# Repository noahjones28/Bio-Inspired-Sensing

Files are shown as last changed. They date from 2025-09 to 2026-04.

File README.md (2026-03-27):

# Bioinspired Backbone Geometry for Continuum Robot Force Estimation

**Noah Jones**

---

## What is this?

Surgical continuum robots often brush against tissue at multiple points simultaneously. Knowing *where* and *how hard* those contacts are is critical for patient safety — but getting that information is hard. Body-mounted force sensors are bulky, hard to sterilize, and impractical at small scales. Base-mounted sensors are practical, but typically don't provide enough information to recover all the contact variables.

This project takes a different approach: **encode the missing information directly into the shape of the robot backbone.** Inspired by the evolved geometry of animal whiskers (rats, seals, elephants), we treat the backbone's cross-sectional profile as a design variable and optimize it so that a single proximal force/torque sensor can uniquely recover multiple 3D contact forces along the body.

<p align="center">
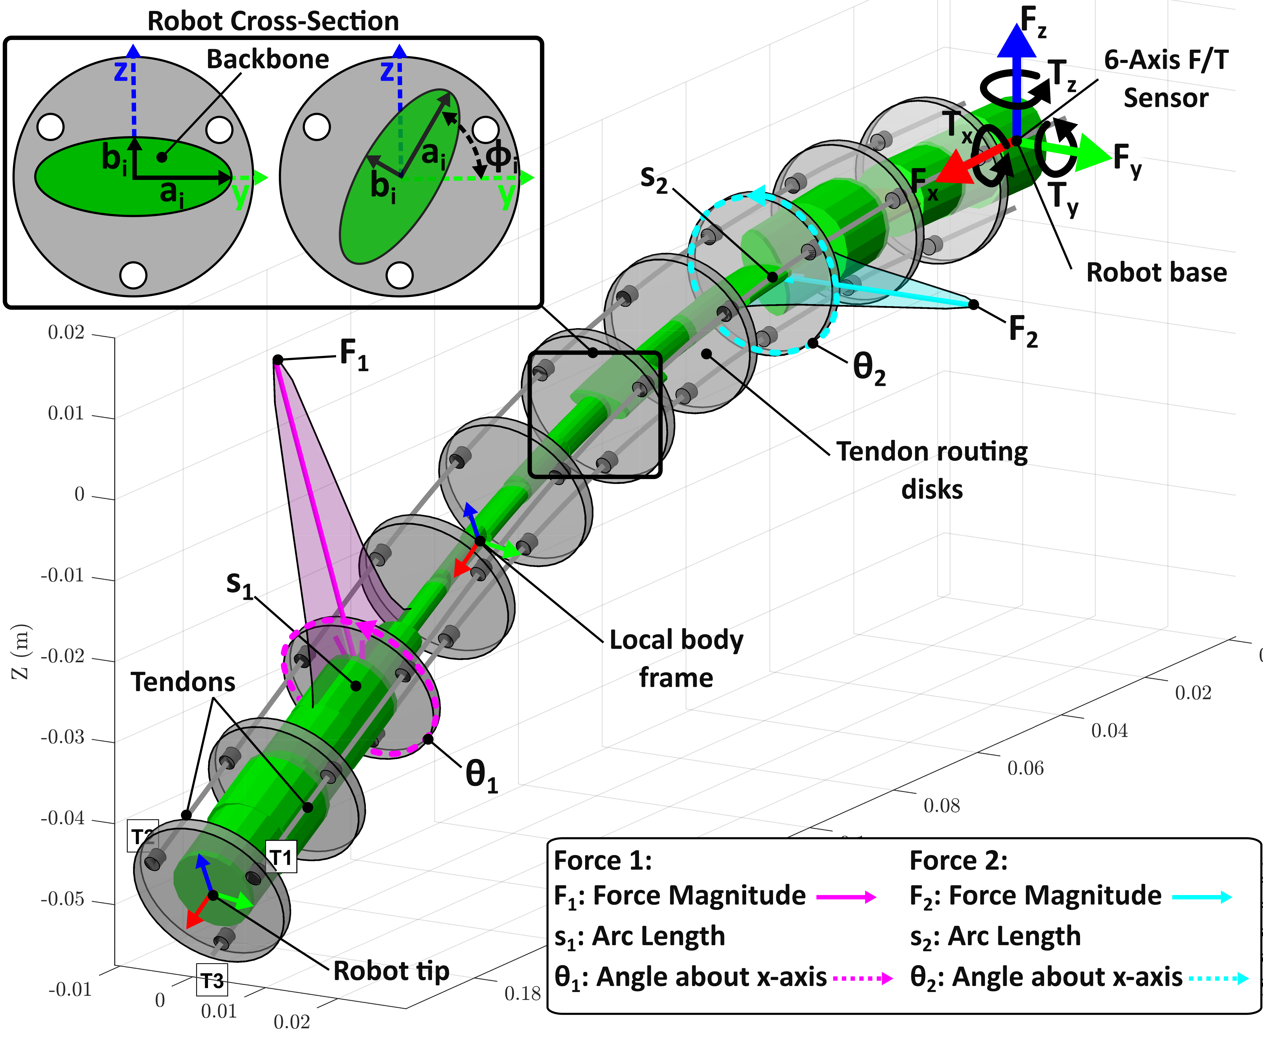
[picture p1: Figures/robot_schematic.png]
  
</p>

*The robot backbone (200 mm, 20 links) is deflected by two simultaneous point forces, each parameterized by magnitude F, arc-length position s, and angle θ. A single 6-axis F/T sensor at the base measures the resulting wrench.*

---

## Key Results

Optimized geometries dramatically outperform conventional cylindrical backbones for multi-force estimation:

<p align="center">
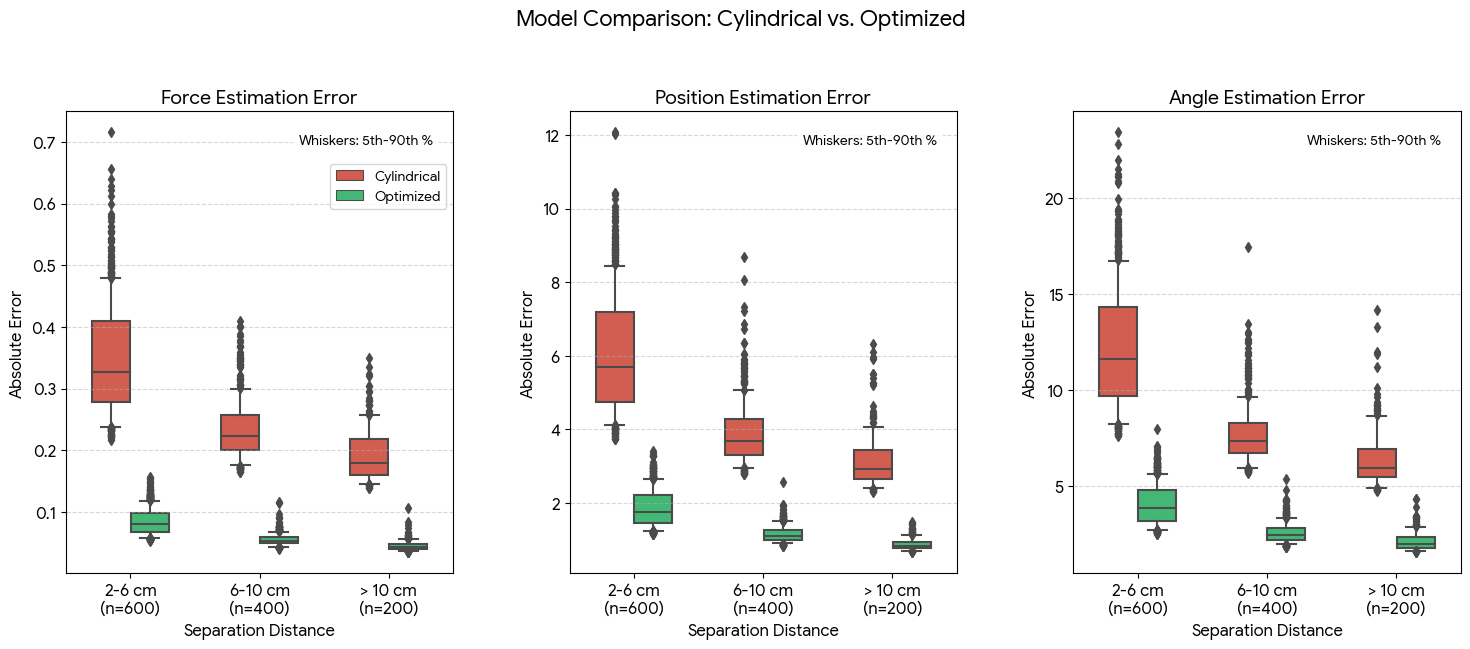
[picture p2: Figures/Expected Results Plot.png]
  
</p>

| Metric | Cylindrical | Optimized | Improvement |
|---|---|---|---|
| Mean force error | 0.22 N | 0.04 N | **~5.5×** |
| Mean position error | 4.97 cm | 0.93 cm | **~5.3×** |

---

## How It Works

### Forward Model

Each link is parameterized with an elliptical cross-section (semi-axes `a`, `b`, rotation `φ`). The backbone is simulated using **SoRoSim** (MATLAB, Cosserat rod theory). Applied forces are modeled as narrow Gaussian distributions rather than true point loads — this dramatically improves numerical conditioning in the inverse solver.

<p align="center">
  
</p>

`forward_model(F, τ)` takes applied forces and tendon tensions → returns the 6-DOF proximal wrench `[Tx, Ty, Tz, Fx, Fy, Fz]`.

### Inverse Model

`inverse_model(Wm, τm)` runs a two-stage solver to recover the forces from a measured wrench:

1. **Global search** — Latin Hypercube Sampling generates 400 candidates across the bounded design space; the 5 lowest-residual candidates become seeds.
2. **Local refinement** — MATLAB trust-region-reflective nonlinear least squares refines each seed to tolerance `10⁻¹⁰`. Best result is returned.

### Design Optimization

`design_optimization.m` searches over 60 design variables (3 per link × 20 links) to find the backbone geometry that minimizes the Jacobian condition number κ(J) — averaged over 60 randomly sampled load cases. A Von Mises safety constraint prevents plastic deformation (Bambu PC, σ_yield ≈ 62 MPa). Uses LHS global search followed by SQP (`fmincon`).

---

## Hardware

<p align="center">
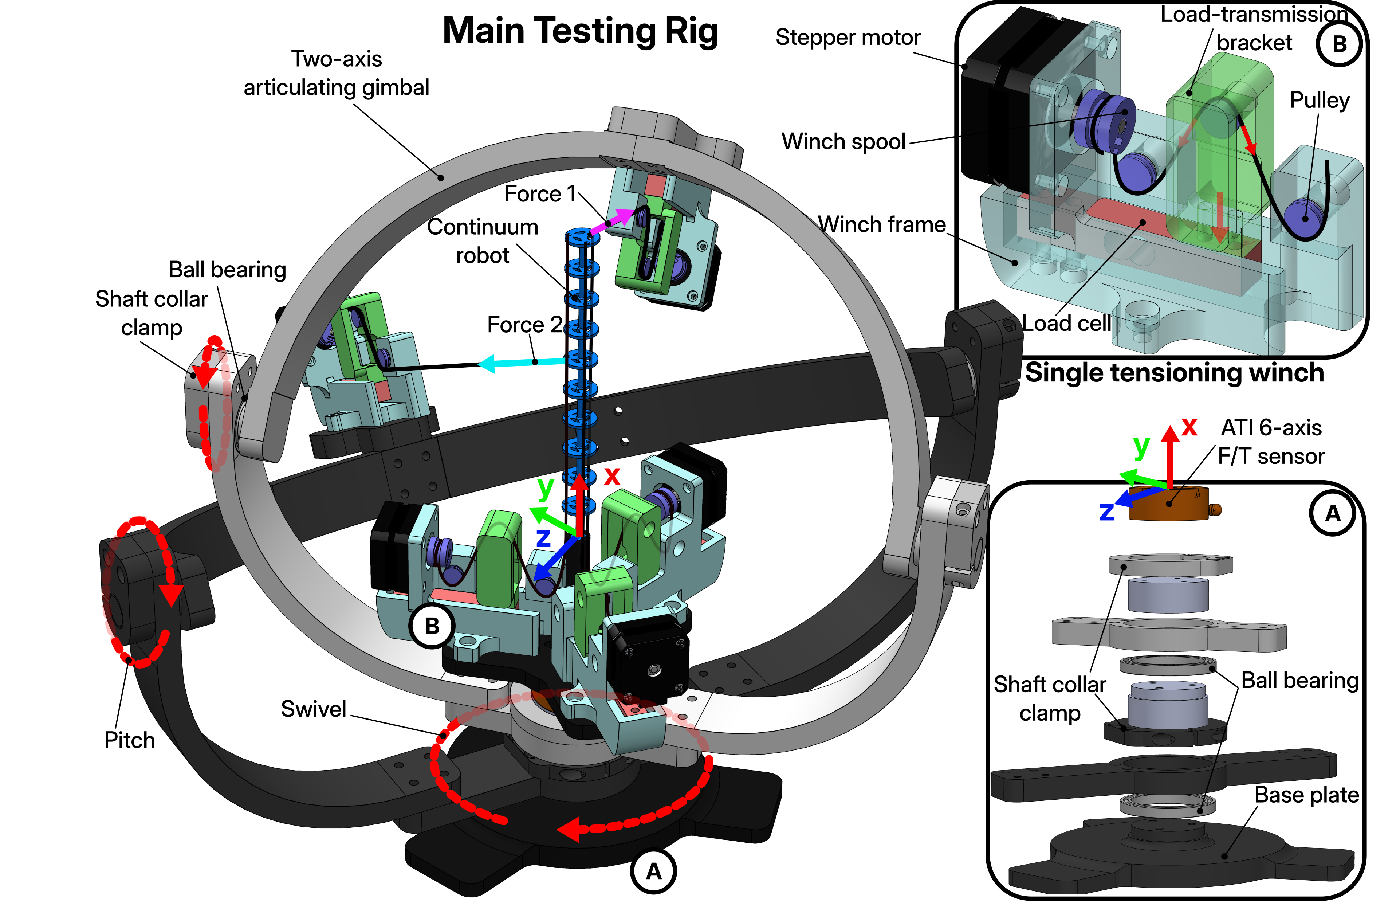
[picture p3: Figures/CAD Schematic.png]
  
</p>

The custom test rig applies two independent 3D point forces simultaneously using:

- **Two-axis articulating gimbal** for arbitrary force direction
- **5× tensioning winches** (NEMA 17 + TMC2209 drivers, 256 microstep)
- **5× 1 kg load cells** with HX711 ADCs for tension feedback
- **ATI Mini40 IP65** 6-axis F/T sensor at the proximal end
- **Arduino Mega** running the author-created control script

The backbone is FDM 3D-printed in Bambu Lab Polycarbonate (PC) on a Bambu X1 Carbon. The SolidWorks parametric model is driven by an Excel Design Table, so printing a new geometry is as simple as exporting the optimized design vector.

---

## Repository Structure

```
forward_model.m              # Applies forces + tendon tensions → proximal wrench (SoRoSim wrapper)
inverse_model.m              # Recovers forces from measured wrench (2-stage nonlinear least squares)
forward_model_parallel.m     # Parallelized forward model for batch evaluation
inverse_model_parallel.m     # Parallelized inverse model
design_optimization.m        # Backbone geometry optimizer (LHS global + SQP local)
compute_jacobian.m           # Finite-difference Jacobian ∂W/∂F
apply_gaussian_force.m       # Converts point loads to discrete Gaussian distributions
calc_ellipse_vonmises.m      # Von Mises stress for elliptical cross-sections (safety check)
global_to_local.m            # Coordinate frame transforms
update_design.m              # Applies a design vector to the SoRoSim robot model
plot_robot.m                 # Visualizes deflected backbone, tendons, and applied forces
jacobian_tester.m            # Validates Jacobian computation
copyHandle.m                 # Deep copy for MATLAB handle objects
my_robot.mat                 # Saved baseline robot configuration

Arduino/                     # Arduino Mega control script (winches + load cells)
ATI Sensor Calibration/      # ATI Mini40 calibration files
CAD/                         # SolidWorks parametric backbone and test rig models
Figures/                     # Publication figures
Optimization Results/        # Saved optimizer outputs
my_robots/                   # Saved SoRoSim robot configurations
```

---

## Dependencies

- MATLAB R2023+ with:
  - [SoRoSim toolbox](https://github.com/SoRoSim/SoRoSim)
  - Optimization Toolbox (`fmincon`, `lsqnonlin`)
  - Statistics and Machine Learning Toolbox (Latin Hypercube Sampling)
- Arduino IDE (for hardware control)

---

## Citation

```bibtex
@mastersthesis{jones2025whisker,
  title  = {Bioinspired Backbone Geometry for Continuum Robot Force Estimation},
  author = {Jones, Noah},
  school = {University of California San Diego},
  year   = {2025}
}
```

---

**Noah Jones** · noah@familiajones.org

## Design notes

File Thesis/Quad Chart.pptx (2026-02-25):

## Bio-Inspired Backbone Geometry for Multi-Point 3D Force Estimation in Continuum Robots

- Problem

- Approach

- Results

- Significance

Noah Jones, T.K. Morimoto

- Motivation: Knowledge of robot-tissue interaction forces during surgery can reduce patient injury and improve quality of surgeon’s force feedback.
- Goal: Estimate the magnitudes and locations of multiple point forces.
- Body-Mounted Sensing (FBGs, EM, Resistive flex):
- Pros: Very accurate Cons: Hard to sterilize, bulky, hard to integrate [1].
- Visual-Based Sensing (Endoscopic cameras, fiducial tracking) :
- Pros: Can resolve multiple point forces with high accuracy [2][3], easy to sterilize.
    - Cons: Requires direct line-of-sight of robot body, camera space constraints.
  - Proximal-Mounted Sensing (force/torque sensors, Tendon tension sensors):
    - Pros: Works in blind environments, easy to sterilize, easy to integrate [4]
    - Cons: Current approaches cannot resolve magnitudes and locations of multiple point forces (ill-posed inverse).

- Design Evaluation: We compare designs numerically and graphically using manipulability ellipsoids. Superior geometries maximize the shortest axis (minimum singular value), ensuring sensitivity in all directions.
- Experimental Validation: For inter-force separations greater than 8 cm, the optimized design achieves median absolute errors of approximately 0.05 N, 1.0 mm, and 2.2°—corresponding to performance improvements of 74%, 67%, and 66% respectively over the cylindrical baseline. Performance gains diminish at smaller separations but remain measurable.

- Idea: We propose estimating multiple point forces using proximal sensors and variations in robot backbone geometry.
- Inspiration: Sensory appendages in animals (whiskers, antennae) use non-circular cross-sections and mass asymmetry to mechanically amplify weak signals—like torsion—that would otherwise be masked by dominant bending modes [5]. These geometries help overcome the ill-posed nature of multi-force sensing in straight cylindrical designs [6][7].
- Method: We develop an optimization framework to find backbone geometries that maximize multi-contact force estimation accuracy. The backbone is modeled as a series of elliptical cross-sections, with the major and minor radii of each segment as design variables. The objective is to find geometries with well-conditioned Jacobians—ensuring sensor noise is not amplified into large force estimation errors.

- Sensing Through Shape: Just as natural selection has shaped animals' sensory appendages to optimize perception for their specific environments, we extend this principle to design tendon-driven surgical robots with geometries tailored to the complex loading conditions they encounter.
- Optimization: We show how optimization can be used to find an optimal backbone design, capable of resolving multiple point-loads that conventional cylindrical backbones cannot due to inherent sensing degeneracies.
- Hardware Testing: We develop a custom testing rig featuring multiple PID controlled tensioning winches and a two-arm gimbal, capable of applying 3 tendon tensions, and 2 point-forces in 3D.

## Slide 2

References

1. Gao, Anzhu, et al. "Body contact estimation of continuum robots with tension-profile sensing of actuation fibers." IEEE Transactions on Robotics 40 (2024): 1492-1508.
2. Aloi, Vincent, et al. "Estimating forces along continuum robots." IEEE Robotics and Automation Letters 7.4 (2022): 8877-8884.
3. Ferguson, James M., D. Caleb Rucker, and Robert J. Webster. "Unified shape and external load state estimation for continuum robots." IEEE Transactions on Robotics 40 (2024): 1813-1827.
4. Sadati, SM Hadi, et al. "Stiffness imaging with a continuum appendage: Real-time shape and tip force estimation from base load readings." IEEE Robotics and Automation Letters 5.2 (2020): 2824-2831.
5. Mohren, T. L., et al. "Coriolis and centrifugal forces drive haltere deformations and influence spike timing." Journal of the Royal Society Interface 16.153 (2019): 20190035.
6. Starostin, E. L., V. G. A. Goss, and G. H. M. van der Heijden. "Whisker sensing by force and moment measurements at the whisker base." Soft Robotics 10.2 (2023): 326-335.
7. Huet, Lucie A., John W. Rudnicki, and Mitra JZ Hartmann. "Tactile sensing with whiskers of various shapes: Determining the three-dimensional location of object contact based on mechanical signals at the whisker base." Soft robotics 4.2 (2017): 88-102.

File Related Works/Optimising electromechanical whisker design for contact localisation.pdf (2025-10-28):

Sensors & Actuators: A. Physical 376 (2024) 115591 (https://doi.org/10.1016/j.sna.2024.115591)

## Available online 12 June 2024

0924-4247/© 2024 The Authors. Published by Elsevier B.V. This is an open access article under the CC BY license (http://creativecommons.org/licenses/by/4.0/).

Contents lists available at ScienceDirect (https://www.journals.elsevier.com/sensors-and-actuators-a-physical)

# Sensors and Actuators: A. Physical

journal homepage: www.journals.elsevier.com/sensors-and-actuators-a-physical

## Optimising electromechanical whisker design for contact localisation

## Simon P. Pegoli a,∗ , Phillip S.M. Skelton a,b , Russell S.A. Brinkworth a

a Centre for Defence Engineering Research and Training, Flinders University, Tonsley, SA, 5042, Australia
b Faculty of Science, Technology, Engineering, and Mathematics (STEM), University of South Australia, Mawson Lakes, SA, 5095, Australia

A R T I C L E I N F O

Keywords:
Electromechanical whisker
Vibrissae
Tactile sensing
Bio-inspired sensing
Object localisation
Robotic mapping

A B S T R A C T

Electromechanical whiskers are inexpensive and useful tactile sensor systems for robotic mapping tasks within environments problematic to image and range sensors. This research aims to quantify the effect of the whisker’s mechanical properties on its ability to achieve accurate contact localisation. Using mechanical beam theory, a model relating the rate of change of a whisker’s strain as a result of the location of a radial contact was derived. A more practical linear approximation of this model was then created with an operating range for which a whisker was theoretically capable of performing contact localisation within 0.1% error. These models facilitated the design of theoretically optimal whiskers. It was discovered that the longer the whisker, and the closer the strain-measuring sensor was placed towards the whisker base, the greater the required taper. For larger whisker widths and faster contact speeds, a smaller taper was required. Additionally, whiskers tapered in 2 dimensions required larger tapers than one-dimensional tapers to achieve optimal performance. The presence of a central hollow region (medulla) did not have a practical effect on the required taper or the performance of the whisker. Experimental results showed that a 200 mm whisker with an optimal taper derived from our model was able to measure the location of contacts with an error less than the target 0.1% anywhere in the distal 58 mm, with a response time of 0.1 s. Tapering electromechanical whiskers to their derived optimal value enhances the accuracy and efficiency of whisker-based robotic mapping.

### 1. Introduction

The ability for mobile robots to autonomously plan and execute navigation using knowledge of their surroundings gathered from on-board sensors has enabled them to be effective in many modern day affairs including inspection [1], search and rescue [2], entertainment [3] and sanitation [4], among many others. The simultaneous localisation and mapping (SLAM) method is used to informedly perform live navigation based on an environment map generated simultaneously using on-board sensors and robotic mapping [5].
The majority of modern robotic mapping approaches utilise optical rangefinders (e.g., light detection and ranging sensors) or vision sensors (e.g., cameras) [6]. Robotic mapping can be enhanced through the implementation of tactile sensing in environments notoriously precarious for optical sensing, including those containing occluded and concealed objects [7,8], compliant and/or malleable bodies [9], particulate air [10] and reflective and/or transparent surfaces [11]. A major disadvantage of tactile sensors is their comparatively shorter search range than optical or visual sensors due to their reliance on physical interaction with external bodies [12]. However, in contrast to range and imaging sensors, whiskers are not only inexpensive and

∗ Corresponding author.

E-mail address: simon.pegoli@flinders.edu.au (S.P. Pegoli).

simple to construct, but require significantly less computational power to operate.
Mammalian facial whiskers (vibrissae) are tactually-sensitive hairs that provide tactile exteroception in almost all mammals [13]. Many small quadrupedal mammals use the information from vibrissae to guide locomotion [14]. Rats commonly feature arrays of between 30 to 35 macrovibrissae of length ranging between 4 mm and 50 mm on either side of the snout [15,16] (2%–23% of the mean length of the brown rat, 217 mm [17]). Rat whiskers can be approximated as truncated cones, and contain a low density region known as the medulla within the proximal portion [18]. The tapered profile enables whiskers to slip past objects once a critical bending angle has been realised [19], enhancing mobility through cluttered environments, whilst the medulla reduces sagging due to gravity [20]. The length and diameter of both the cuticle and the medulla vary based on the location of the whisker on the mystacial pad, and has been quantified in [21]. The formation of whiskers on the mystacial pad forms 2 search volumes on either side of the snout with a shape resembling sections of spheres centred about the rat’s eyes [22]. Rats will actively sweep (whisk) their whiskers in front of them in the azimuth direction to induce light contacts with external objects [23,24], further expanding the whisker search

https://doi.org/10.1016/j.sna.2024.115591
Received 20 February 2024; Received in revised form 18 May 2024; Accepted 9 June 2024

## Sensors and Actuators: A. Physical 376 (2024) 115591

S.P. Pegoli et al.

volume. Behavioural studies indicate that rats will whisk in a manner to purposefully make contact at radial locations near to, and at, the whisker tip [24].
Two different types of mechanoreceptive cells are located in the whisker follicle, allowing for the detection of both the magnitude and rate of change of the whisker deflection [25,26]. Neurological processing of the mechanoreceptor signals, proprioceptive knowledge of whisker locations on the snout, and the timing of the contact during the whisk cycle allows rats to determine the spatial location of a contact [27,28]. Through this, rats can recognise both the shape [15] and orientation [29] of objects.
Contacts made on an electromechanical whisker can be localised by deciphering the mechanical response of the whisker measured by a variety of sensors. Selection of the sensor device(s) used, the whisker shaft material, and the manufacturing process are key design choices for electromechanical whiskers, and are often intertwined. Following the foundational concept that animal nervous systems are more adept at measuring the rate of change of signals rather than their absolute magnitude, the rate of change of the whisker strain [30] or the bending moment [31] collected by strain gauges can be converted to a contact location for whiskers arranged as cantilever beams. In the case of the whisker strain, this holds true as long as the whisker undergoes small deflections, e.g., less than 10 degrees [30]. Similar outcomes can be achieved through measurement of the pressure on a load plate perpendicular to the whisker shaft using barometers [32,33] and piezoresistors [34]. Measurement of the degree of deformation throughout the whisker shaft can be used, achievable by measuring the wavelength shift due to bending of optical fibre [35]. For a hinged whisker, the displacement of the whisker base in multiple dimensions can be used to convert whisker shaft deformation into a contact location using Hall effect sensors [36,37]. A hinged whisker is seemingly more complex to develop than a cantilever beam due to the requirement for an automatic return system, which can be especially challenging to achieve at small scales. Many other designs utilising different sensing modalities also exist (see [38] for a recent review covering electromechanical whisker designs). In all of these cases, the signal magnitude varies non-linearly with the contact location.
The whisker shaft can be manufactured simply as beams from plastic rods [32,34] or metal wires [31,37]. Curvature can be achieved through heat-forming [37]. 3D printing [33,39] and moulding [30] allows for precise manufacturing of whiskers with various shapes. Thermoplastics often used in 3D printing, such as acrylonitrile butadiene styrene (ABS), possess favourable mechanical properties which allow whiskers to deflect elastically at large angles (up to at least 50 degrees) without permanent (plastic) deformation [40], which can be useful for operation within confined spaces. Fibre drawing of thermoplastics can achieve desired tapering of whiskers at smaller scales than conventional fused deposition modelling [40]. The whisker can be formed entirely from the sensor system itself, as in the case for optical fibre whiskers [35], and embedding such sensors within a material can control its deformation properties whilst protecting the sensor from the external environment [41,42].
Maps can be generated using electromechanical whisker sensing through the collection of localised contact locations in space over the duration of a navigation mission. Contour fitting allows for the reconstruction of object shapes using localised whisker contact points [8,31,35]. Modelling of a robot’s searched environment can be achieved through population of an occupancy map using recorded whisker contact points, achievable using SLAM techniques [43–45]. Texture sensing is another heavily explored application with electromechanical whiskers, allowing for discrimination of objects based on their surface smoothness [46–48].
Both the bending moment and the strain along the whisker increases in direct proportion to the whisker’s base diameter and the contact speed [30,31]. As the width of the whisker increases, however, so will its rigidity [49]. For rats, the conical whisker taper is an important functional feature as this allows objects to conveniently slip past the whisker without inducing large, potentially damaging bending angles, enabling agile mobility within their typically confined and cluttered habitats [19,50]. Untapered whiskers will also frequently become stuck inside the grooves of textured surfaces, whereas tapered whiskers, especially conical, will undergo characteristic stick–slip behaviour, indicating a greater applicability of tapered whiskers to feature sensing [50]. For electromechanical whiskers, the three-dimensional (3D) contact location can be uniquely calculated using the combination of the axial force, the bending moment magnitude, and the direction of the bending moment measured at the whisker base, as long as the whisker is tapered [51]. 3D contact localisation has been found to be more accurate for tapered whiskers than untapered whiskers when using these same mechanical measurements [40]. A ‘‘sweet spot’’ between the location of object contact and the contact speed for which discrimination of contacts are more easily achieved is suggested to exist [52]. However, this balance has not been identified across the various parameters that make up a whisker system.
Aside from these observations, the impact of an electromechanical whisker’s geometry and other design/functional parameters on its capability to localise contacts has, to the best of our knowledge, yet to be quantified. The goal of this research was to universally quantify the optimal balance between whisker length, thickness, taper, and whisk speed for achieving accurate contact localisation. The impact of the presence of a medulla was also explored. This was with specific interest towards whisker systems that can achieve accurate localisation as efficiently as possible, requiring minimal computing resources for signal processing. This knowledge will enable roboticists to efficiently design electromechanical whisker systems that can attain optimal contact localisation results, improving robotic mapping outcomes.

### 2. Materials and methods

### 2.1. Whisker parameters and nomenclature

Figs. 1(a) and 1(b) show, respectively, the front and top view of a schematic electromechanical whisker of length lw, base width wb

, and
tip width wt undergoing contact by an object at distance l
c

from the
whisker base with contact speed vc

. Our approach treated whiskers as straight, homogeneous, flexible cantilever beams due to the simplicity in manufacture of a cantilever whisker compared to a hinged whisker. In a similar fashion, the whisker strain, measurable through a single sensor element such as a strain gauge placed at a distance l
s

from the
whisker base, was used as the sensory input for contact localisation as this requires straightforward assembly with simple circuitry and signal processing as opposed to other methods.
The whisker’s taper magnitude (T ) was defined as the ratio of the cross-sectional area of the outer shape of the whisker base (Ab
) to
the cross-sectional area of the outer shape of the whisker tip (At ),
disregarding any holes present in either of the cross-sections, as per Eq. (1).

T =

Ab
At

(1)

We explored 2 categories of whisker taper: (1) tapered in a single dimension (T1D); and (2) tapered in 2 dimensions (T2D). A T1D whisker was one whose height remains constant but whose width decreases along the whisker length (represented as a dashed line in Fig. 1). A T2D whisker was one in which both the width and the height decreased uniformly along the whisker length (represented as a solid line in Fig. 1), e.g., a cone. Whiskers with no taper (i.e., T = 1), e.g., a cylinder, were classified as untapered (T0D). This research only considered whiskers with a linear taper with the base’s external cross-section having regular shape (i.e., a regular polygon or a circle). Both T1D and T2D taper types were explored as we hypothesised that they would each provide distinct advantages in different situations. T1D whiskers, being more

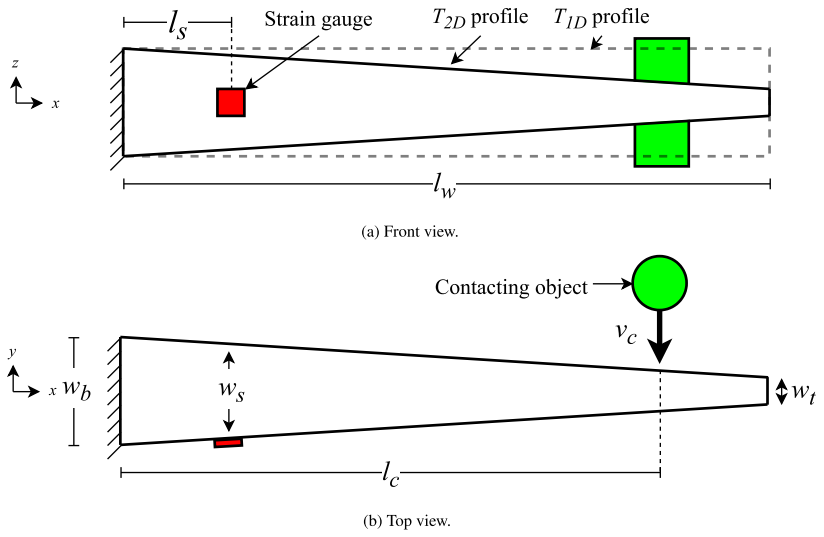
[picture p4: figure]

Fig. 1. Schematic of a T1D (dashed profile) and T2D (solid profile) whisker of length lw, base width wb and tip width wt , undergoing contact at length l
c

from the whisker base
at contact speed vc
. l
s

represents the distance between the whisker base and the centre of the sensing element, with ws being the width of the whisker at this location. (a) Front view. Only T2D whisker tapers in height. (b) Top view. Both T1D and T2D whiskers taper in width.

flexible in the direction of the contact (y axis) than in the perpendicular
direction (z axis), would be expected to be more suitable to applications
where only unidirectional contacts were of interest, as deflection in the perpendicular direction would be more restricted. T2D whiskers, being flexible in both the y and z directions, were expected to be more suitable for measuring contacts occurring in both planes.

### 2.2. Derivation of whisker strain relationship to contact location

Under the assumption that the contacting object is rigid and applies a point load to the whisker during contact, the Euler–Bernoulli beam equation [49] can be used to derive a numerical relationship between the whisker strain and the contact location. For a small deflection in the y direction (s) at the contact location (l
c

) arising from a point load (F) (e.g., a rigid body contact), the curvature (κs

) of a cantilever beam
(whisker) measured at a point on the whisker face along the x axis (l
s

)
is given as:

κs ≈

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
c − l
s

)
EIs
, | (2)

where Ms

is the moment at point l
s
| , E is the Young’s modulus of
the whisker, and Is

is the second moment of area at point l
s
| in the
direction perpendicular to the contact. Study of the geometry of tapered beams shows that the width of the whisker at the sensor location (ws
| )
is related to the whisker base width (wb | ), total length (lw), and the
distance of the sensor from the base (l
s

) by:

ws1D

= wb

(
1 +

l
s
lw

(1∕T − 1)

)
| (3a)

ws2D

= wb

(
1 +

l
s
lw

(√

1∕T − 1)) | (3b)

where ws1D

is the whisker width at the sensor location for a T1D whisker, and ws2D

is that for a T2D whisker. Is | can therefore be written
as the product of the second moment of area at the whisker base (Ib
| )
and the scale of diversion of the second moment of area at the sensor location from that at the whisker base (∇I), as in Eq. (4):
Is = Ib∇I | (4)

∇IT1D

=

(
1 +

l
s
lw

(1∕T − 1))3
(4a)

∇IT2D

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
1∕T − 1))4
(4b)

where ∇IT1D

is the scale of diversion of the second moment of area at the sensor location from the whisker base for a T1D whisker, and ∇IT2D is that for a T2D whisker. This relationship holds true for both solid and hollow whiskers, as long as the taper magnitude of the hollow geometry matches the taper magnitude of the whisker’s shaft.
Substituting Eq. (4) into Eq. (2), taking the definite integral from points 0 to l
s

twice to solve for the whisker displacement, and solving for the contact location, an equation for the deflection at the contact location (sT

) can be obtained for both taper classes:

sT1D

(l
c

) =

F lw(a1

2
l
c

2 + 2lw

2
(ln(a1
l

c + lw) − ln(lw)) − 2a1
l
c

lw)
2a1

3EIb

(5a)

sT2D

(l
c

) =

F lc

2
lw(2l
c

2
a2 + 2l
c

lw)
6EIb

(l

ca2 + lw)

2

(5b)

where a1 = 1∕T − 1 and a2 =

√
1∕T − 1. The whisker strain at the sensor location (εs

) is related to the moment at l
s

(Ms

), section modulus
at the sensor location (Zs

), and Young’s modulus of the whisker (E) by Eq. (6):

εs =

Ms
ZsE

=

F(l

c − l
s

)
ZsE

(6)

Rearranging Eq. (6) for F and substituting into Eq. (5), the displacement at the contact location can be expressed in terms of the whisker strain measured at the sensor location:

sT1D

(l
c

) = εs ×

lwZs

(2lw

2
ln(a1
l

c + lw) + a1
l
c

(a1
l

c − 2lw) − 2lw

2
ln(lw))
2a1

3Ib
(l

c − l
s

)
(7a)

sT2D

(l
c

) = εs ×

l
c

3
lwZs
3Ib

(l

c − l
s

)(l

ca2 + lw)

(7b)

Solving Eqs. (7a) and (7b) for εs and taking the time derivative on both sides, the relationship between the rate of change of strain ( ̇εs )
and the whisker contact location is:

̇εsT1D

(l
c

) = vc ×

2a1

3Ib
(l

c − l
s

)

lwZs

(2lw

2
ln(a1
l

c + lw) + a1
l
c

(a1
l

c − 2lw) − 2lw

2
ln(lw))
(8a)

̇εsT2D

(l
c

) = vc ×

3Ib

(l

c − l
s

)(l

ca2 + lw)

l
c

lwZs

(8b)

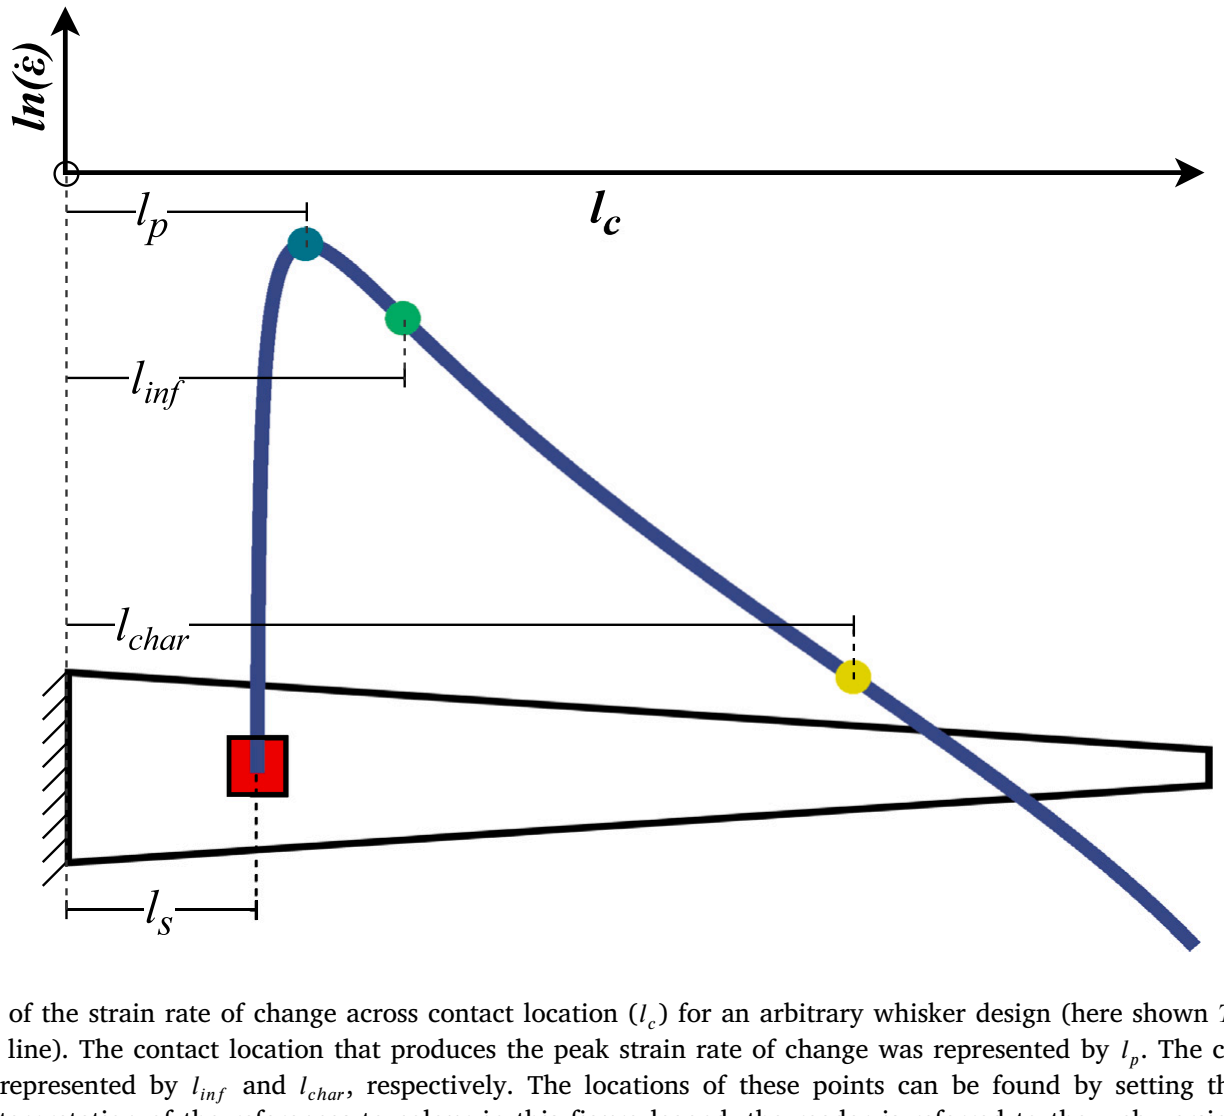
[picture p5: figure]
inf and l

Fig. 2. General shape of the logarithm of the strain rate of change across contact location (l
) for an arbitrary whisker design (here shown T2D taper, refer to Section 2.1) overlaid over the whisker (blue solid non-linear line). The contact location that produces the peak strain rate of change was represented by lp

. The contact locations of the first and second (characteristic) inflection points were represented by l

cℎar , respectively. The locations of these points can be found by setting the first (lp

) and second (l

inf and l
cℎar )
derivatives of Eq. (8b) to zero. (For interpretation of the references to colour in this figure legend, the reader is referred to the web version of this article.)

If the contact velocity (vc

) is known, which is achievable by performing controlled motorised whisks, solving Eqs. (8a) and (8b) for l
c
can therefore be used to deduce the contact location from the rate of change of the whisker strain at location l
s

for small whisker deflections. It is important to note that Eq. (8a) is invalid for a T0D whisker as it means a1 = 0, which results in ̇εsT1D

= 0, which is untrue. Therefore Eq. (8b) must be used for untapered whiskers. It is also important to note that the shape of the whisker’s cross-section does not feature in the equations. Therefore, the rate of change of the strain is independent of the cross-sectional shape for whiskers within the same taper class which have a uniform taper. Additionally, Eqs. (8a) and (8b) show that ̇εs does not depend on the whisker’s material (i.e., the Young’s modulus). This is as the equations assume that the whisker’s (or inversely the object’s) translational velocity remains constant during the contact, and that the bending of the whisker during the contact does not contribute to a reduction in this velocity. This is practically suitable assuming that the contacting object is rigid and the whisker is flexible enough to not undergo plastic deformation from the applied displacement.

### 2.3. Linearising the model

Fig. 2 shows the general shape of the logarithm of the strain rate of change across contact location curve for a whisker of arbitrary length, taper, width, and sensor location.
The shape of the logarithm of the strain rate of change across contact location reveals three fundamental points along the curve: Location of the peak strain rate of change lp

; location of the first inflection point l

inf ; and location of the second inflection point l

cℎar. Firstly, the strain
rate of change rapidly increases for contact locations further along the whisker length than the sensor location before reaching a peak at location lp

, for which the strain rate of change decreases beyond. The contact location producing this peak indicates the lower limit of the total operating range of the whisker, as contacts towards the whisker base from this point will produce non-unique strain rate of change with contacts towards the whisker tip, making the contact location ambiguous.
The first inflection point, l

inf , exists a short distance following the peak. However, its value was not important to our method. The second

inflection point, l

cℎar, exists towards the whisker tip. This second inflection point was of importance for obtaining a linear approximation of the whisker’s strain rate of change across contact location, and will henceforth be referred to as the characteristic inflection point. Deriving a linear approximation centred at this point will create a linear operating range towards the whisker tip, which was desirable for mapping purposes.

The linearised model of the logarithm of the strain rate of change across contact location was calculated for T0D, T1D and T2D whiskers as the first order Taylor series centred about the whisker’s characteristic inflection point. The operating range for a whisker’s linear model was defined as the region of the whisker for which the percent error between the strain rate of change curve and the first order Taylor series approximation was within 0.1%. This maximum error was selected to promote high accuracy within the entirety of the linear operating range.

A whisker’s optimal taper (T

∗
) was defined as that which possessed the widest linear operating range that included the whisker tip, thus maximising the operating range. This range also enables mimicry of rat whisker placement behaviour which is biased towards contacts near and including the tip [24]. T

∗ was calculated by finding the smallest whisker taper that possessed a linear operating range whose upper limit was located exactly at the whisker tip. Generalised mathematical models describing T

∗
, the corresponding size of the linear operating range (W ∗
) and location of the characteristic inflection point (l

∗
cℎar),
were developed by calculating these values for whiskers of varying length, sensor location, base width and contact speed for both T1D and T2D whiskers. The sensor location was limited to within 1/8th of the whisker length from the base as sensors placed within this region would have reduced potential for collision with objects during robotic mapping tasks.

The effect of deviating from the optimal taper on whisker-based robotic mapping was observed by plotting the linear operating size range against the proportion of whisker taper against the optimal whisker taper. This was performed for both T1D and T2D whiskers across varying sensor location, whisker length, base width and contact speed.

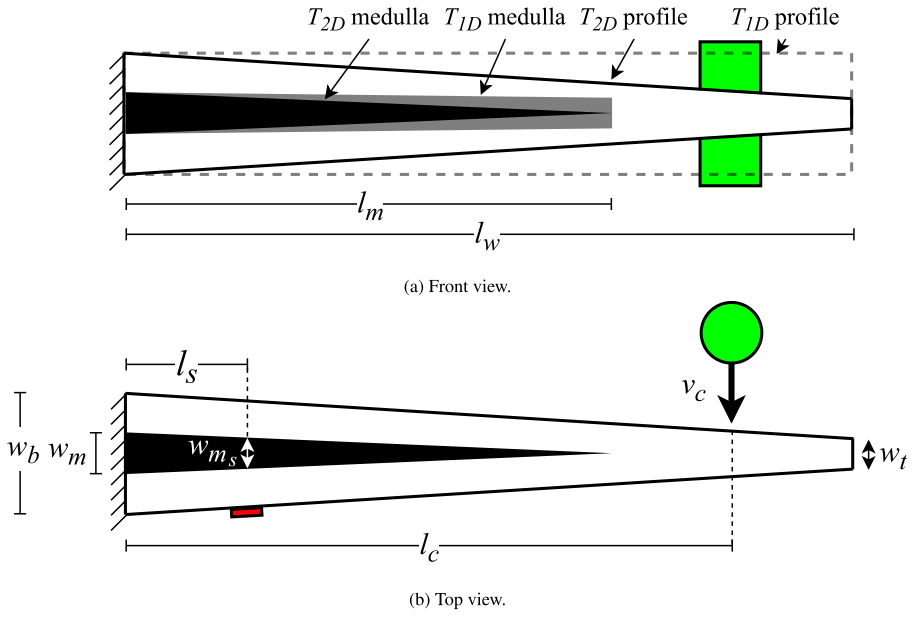
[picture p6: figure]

Fig. 3. Schematic of the central cross-section of whiskers with a biologically mimetic medulla (shaded area) with base width wm and length lm
. The darker shaded region shows the shape of the medulla for T2D whiskers, and the lighter shaded region shows the shape of the medulla for T1D whiskers. The width of the medulla at the sensor location is denoted wms

. (a) Front view. The medulla for T2D whiskers tapers to a point, but the medulla for T1D whiskers tapers to an edge. (b) Top view. The medulla for both T1D and T2D whiskers taper in width.

### 2.4. Exploring the medulla

The effect of a biologically mimetic medulla on whisker performance was explored mathematically. Here, whiskers were now modelled to contain a medulla as a tapered, hollowed-out region centred about the central axis of the whisker. The medulla’s cross-section had the same shape of the cross-section of the whisker shaft, with the widest point at the base, and tapered linearly with the same taper dimensionality as the whisker shaft (i.e., a 1D taper for T1D whiskers and a 2D taper for T2D whiskers) up to an edge (for T1D whiskers) or a point (for T2D whiskers), at a distance lm from the whisker base. Fig. 3 shows the central cross-section of a whisker containing a medulla, showing these parameters. The base width of the medulla (wm), and the length of the medulla (lm), were fixed for any given whisker based on Eqs. (9a) and (9b) respectively, selected based on the average medulla proportions for the column of caudal-most whiskers on the rat snout (i.e., the longest whiskers) [21]. This resulted in the width of the medulla at the sensor location (wms

) being related to the whisker base width, length and sensor location by Eq. (9c).

wm = 0.324wb

(9a)

lm = 0.786lw | (9b)

wms

= wb

(
0.324 − 0.415

l
s
lw

)
| (9c)

The scale of diversion of the second moment of area at the sensor location from that at the whisker base for whiskers not containing a medulla (∇I) was no longer equal to the relationships of Eqs. (4a) and (4b) for whiskers containing a medulla where the taper magnitude of the whisker was such that the slope of the whisker shaft did not match the slope of the medulla. The scale of diversion of the second moment of area at the sensor location from that at the whisker base was derived for T1D and T2D whiskers containing medullae (∇Im), and the ratio of (∇Im) to ∇I for whiskers of the same taper class was taken to quantify the impact of the addition of the medulla on this parameter (see Appendix A for the algebraic derivations of these). This revealed that ∇Im was practically equivalent to ∇I, and therefore Eqs. (8a) and

(8b) were deemed appropriate for calculating the strain rate of change of the whisker due to a contact for whiskers possessing a medulla. The optimal taper, operating range, and characteristic inflection point was modelled for whiskers possessing a medulla using the same method as in Section 2.3. The effect of the medulla on these parameters was quantified by calculating the root mean square error (RMSE) between the models for whiskers with a medulla to those without medullae.

### 2.5. Simulations

Transient structural analyses were performed in Ansys Mechanical 2021 R2 to verify the correctness of the derived strain-contact location relationship. Whiskers were fixed at the base using a fixed body-ground joint, and an 8 mm diameter steel cylinder was driven radially into the whiskers with constant speed at various contact locations (refer to Section 2.1 and Fig. 1 for more details). A cylinder was used to produce a constant translational deflection at a point on the whisker whilst allowing the whisker to slip smoothly past it as it deforms. Note that this causes the contact location to slide towards the whisker tip as the whisker deforms. As we were only interested in the strain relationship over small deflections, the effect of this slippage was negligible. The strain along the whisker length on the side opposite to the contact was measured across time, which was then used to calculate the strain rate of change at potential sensor locations.
Two variations in the whisker cross-sectional shape were studied for the three taper classes (T0D, T1D and T2D) to check for consistency in results for varying whisker profiles. For T0D whiskers, both cylindrical and square prisms were studied. For T1D whiskers, whiskers were designed as a square base tapering to a rectangular tip and a circular base tapering to an ellipsoidal tip (both with constant heights). For T2D whiskers, truncated square pyramids and truncated cones were studied. Three different whisker base widths were simulated to observe the effect of the whisker width: 4.5 mm, 6 mm and 8 mm. These widths were selected as whiskers could be reliably manufactured at these widths for comparison between simulation and hardware.
The resulting strain rate of change data from the simulation results were plotted against the theoretical model to observe the closeness

Table 1
Materials and their respective Young’s modulus (as quantified in Ansys) used in the simulations to determine the effect of whisker material on the strain rate of change.
Material | ABS | PLA | Epoxy resin | Beech wood | Aluminium alloy | Structural steel
Young’s Modulus [GPa] | 2.41 | 2.94 | 3.78 | 12.93 | 71 | 200

of the simulation results to theory. The coefficient of determination (R²
) and RMSE were calculated for each whisker taper to quantify the alignment of the simulation results to the theory.
Simulations were additionally performed to determine whether there was an impact on the strain rate of change relationship with the contact location due to the whisker’s material. The strain at the sensor location was recorded for whiskers of equivalent dimensions but made from different materials. The materials tested, and their Young’s modulus (recorded from Ansys), can be found in Table 1. The resulting strain rate of change during the initial contact period (i.e., small deflection period) was compared for equivalently shaped whiskers of different materials for contacts made at the same location.

### 2.6. Hardware experiments

Experiments were performed with a manufactured ABS whisker with optimal T2D taper to observe the performance of a theoretically optimal whisker in performing contact localisation using the developed linear approximation method. The whisker was manufactured as a truncated square pyramid with wb=4.5 mm and lw=200 mm through fused deposition modelling 3D printing. This method allowed for inexpensive and repeatable whisker production. An alternative approach of printing whiskers from inexpensive resin was found to limit their use in confined spaces due to their tendency to snap at smaller angles than ABS whiskers, and was therefore not used. While specialist resins may have been available, their cost would have been prohibitive. Derivation of the taper magnitude used for this whisker can be found in Section 3.3. A truncated square pyramid was used to promote deflection in the x-y plane and hinder deflection in the x-z plane from a contact in the y direction (see Fig. 1(b)) whilst resembling the T2D geometry seen in rat whiskers. The whisker length was selected such that the whisker could be useful for robotic mapping when aboard a small mobile robot, where a maximum detection range of 200 mm would be sufficient for object avoidance and to cover potential dead zones of LiDARs. The base width selected was the minimum practical base width that allowed for adhesion of a strain gauge (Tokyo Measuring Instruments Lab model FLAB-5-11-1LJC-F) at a sensor location of l

s = 20 mm. This
was the lowest practical sensor location within the targeted bottom 1/8th of the whisker length due to the strain gauge dimensions and wire routing considerations. The strain gauge was wired to an arm of a balanced quarter Wheatstone bridge whose output was amplified with an instrumentation amplifier. The amplified output was connected to a 12-bit analogue to digital converter (ADC) pin of a Teensy 4.1 to measure the resulting resistance change from increasing whisker strain at a sampling rate of 500 Hz (sampling period 2 ms).
Fig. 4 illustrates the experimental setup. The whisker was mounted to a custom steel clamp that clasped a 40 mm extension from the whisker base, forming a cantilever beam with free end of length lw. A motorised linear rail was positioned perpendicular to the whisker which drove a carriage holding a shanked M8 bolt travelling radially to the whisker. The bolt was positioned such that only the smooth, shanked area would make contact with the whisker. The rail was driven at a maximum linear speed of 16 mm/s using a stepper motor. The experimental setup was situated upon an air-stabilised optical fixture table (Newport SmartTable) with the motorised rail fixed in position. The whisker clamp was able to be moved closer to and further from the rail to allow for variable positioning of the contact location.
The measured ADC value from the output of the amplified Wheatstone bridge was sent to a MATLAB script that used to save the transient response of the ADC during the contact. The rate of change of the

ADC value was determined by calculating the temporal derivative. This signal was noisy, so a low-pass filter was used to smooth the result. The filtering used was the fastest first-order infinite impulse response (IIR) time constant that resulted in the difference between average recordings of baseline (no contact) and tip contact being two standard deviations (τ = 0.046 s). This approach was chosen as it could be implemented as a hardware filter if desired. It also had the minimum impact on the dynamics of the system while achieving a functionally useful level of detection accuracy at the whisker tip. An additional tophat analysis window was used to analyse the average transient response of the ADC during contact. The analysis window was measured for a window of fifty samples (0.1 s period) beginning once the filtered ADC derivative transient response reached steady state.
To convert from ADC rate of change to strain rate of change, a scalar equal to the theoretical strain rate of change at the whisker’s characteristic inflection point divided by the average ADC rate of change measured at the characteristic inflection point was used. This single scaling factor was selected as it represented a practical and efficient method of calibrating the hardware sensor rather than taking multiple points along the whisker length.
The strain rate of change was measured for contacts made at the tip down to 40 millimetres above the whisker base at 2 mm spacings. This was limited by the experimental apparatus. Following the singlepoint calibration process, the R² and RMSE of the experimental results compared to the theoretical model were calculated for the whisker to determine the accuracy of the whisker.
The whisker’s measured strain rate of change values were converted to an estimate of the contact location by passing them through the inverse of the whisker’s theoretical linear approximation. Values exceeding the whisker length were clamped to be equal to the whisker length. The error between the estimated contact location and actual contact location was quantified across the whisker length as a measure of the difference between the measured contact location and the real contact location to determine the accuracy of the linearisation approach across the whisker length.

### 3. Results

### 3.1. Optimal whisker taper

The magnitude of the optimal whisker taper (T

∗
) was found to
be dependent on the whisker’s length (lw), base width (wb ), sensor
location (l
s

) and contact speed (vc

). Additionally, it differed for T1D and T2D whiskers. The relationship between these parameters, and the magnitude of the optimal whisker taper, was modelled by Eqs. (10a) and (10b) for T1D and T2D whiskers respectively:

T

∗
1D

≈ lw

0.029 (

3.966 − 2.348 (
l
s
lw

)) −

ln (wbvc

)

(

0.138 − 0.0108 ln (lw) − 0.0692 ( l
s
lw

)) ,

{

0 ≤

l
s
lw

≤ 0.125}

(10a)

T

∗
2D

≈ lw

0.039 (

8.788 − 8.115 (
l
s
lw

)) −

ln (wbvc

)

(

0.401 − 0.028 ln (lw) − 0.275 ( l
s
lw

)) ,
{

0 ≤

l
s
lw

≤ 0.125}

,

(10b)

where the length from the base to the sensor, the total whisker length and the width of the base are in mm and the contact velocity is in mm/s. Refer to Figs. B.1 and B.2 in Appendix B for plots of the

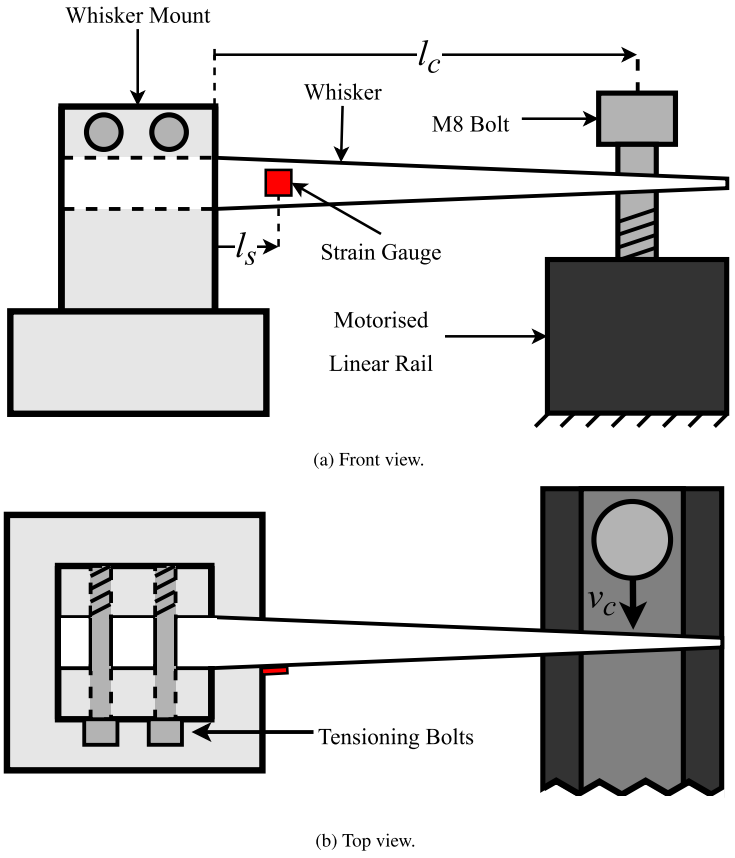
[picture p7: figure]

Fig. 4. Diagram of the experimental setup. A straight extension at the whisker’s rear was fastened inside a steel mount using two bolts to create an interference fit, enabling the free end to act as a cantilever beam with the longitudinal axis parallel with the ground. A shanked M8 bolt was driven radially into the whisker at position l

c along the whisker
length (variable by adjustment of the mount’s location) with contact speed vc by a motorised linear rail to induce a small, constant deflection. (a) Side view. (b) Top view.

calculated optimal taper (from theory) and the approximated optimal
taper (from Eqs. (10a) and (10b)) across the four parameters.
For realistic scenarios (e.g., whisker lengths below 10s of metres, base widths in the order of mm and contact speeds in the order of mm/s to m/s), longer whiskers required marginally larger tapers. Alternatively, a smaller taper was required if the sensor location was placed further from the base of the whisker. A smaller whisker taper was also required as the whisker’s momentum (which scales proportionally with wb and vc

) was increased. T2D whiskers required larger tapers than T1D for equivalent lw, l
s

, wb

, and vc

. However, the rate of change of the whisker’s width along the whisker length was larger for T1D whiskers (i.e., the T1D whisker had a smaller tip width than the equivalent T2D whisker). There was no practical difference in the optimal taper between whiskers with and without medullae, with the RMSE between T

∗ of whiskers with a medulla to those without a medulla being 0.005 for T1D whiskers and 0.008 for T2D whiskers. The generalised models deviated minimally from the calculated optimal tapers, possessing an inherent average error and standard deviation of 0.002±0.015 and −0.009±0.038 for T1D and T2D whiskers, respectively.
Eq. (11) describes the size of the linear operating range for optimally tapered whiskers (W ∗
) in proportion to the total whisker length lw:

W ∗
lw

≈ lw

0.053 (
0.229 + cW + 0.179 (
l
s
lw

)) −

ln (wbvc

)

(

0.025 − 0.00268 ln (lw) + 0.012 ( l
s
lw

)) ,
{
0 ≤

l
s
lw

≤ 0.125}

,

(11)

where l
s

, lw and wb are in mm, vc

is in mm/s and the operating range size constant (cW ) was −0.0056 for a T1D whisker and 0.0056 for T2D whiskers. Refer to Figs. C.1 and C.2 in Appendix C for plots of the calculated linear operating range size (from theory) and the approximated linear operating size (from Eq. (11)) across the four dependent parameters.
The linear operating range as a ratio of the whisker length for optimal tapers was marginally larger for longer whiskers, and increased as the sensor location moved further from the base. However, an increase in the whisker’s momentum lead to a decrease in the size of the operating range. T2D whiskers possessed wider operating ranges than T1D whiskers of equivalent length, sensor location and momentum factor based on the size constant. There was no practical difference in operating range between whiskers with and without a medulla. The average error and standard deviation between the calculated and estimated size was 0.008±0.003 for T1D whiskers and −0.002±0.005 for T2D whiskers.
The location of the characteristic inflection point for optimally tapered whiskers (l

∗
cℎar) as a fraction of whisker length was modelled in Eq. (12):

l

∗
cℎar
lw

≈ lw

−0.00845 (

0.887 + clcℎar

− 0.12 (
l
s
lw

)) +

ln (wbvc

)

(

0.0115 − 0.00123 ln (lw) + 0.00511 ( l
s
lw

)) ,
{
0 ≤

l
s
lw

≤ 0.125}

,

(12)

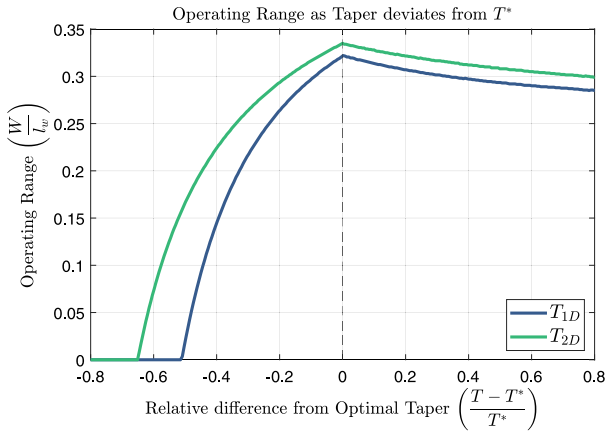
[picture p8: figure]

Fig. 5. Operating range change for varying whisker taper for a T1D and T2D whisker with equivalent length lw = 200 mm, sensor location l

s = 20 mm (0.1lw) and product of base width and contact speed (i.e., momentum) wb × vc = 1 mm²/s.

where l
s

, lw and wb are in mm, vc

is in mm/s per second and the constant of inflection (clcℎar

) was 0.0043 for T1D whiskers and −0.0043 for T2D whiskers. As the characteristic inflection point was the point in which the Taylor series approximation was centred at, this model described the ideal practical contact location for the most accuracy (zero error). Refer to Figs. D.1 and D.2 in Appendix D for plots of the calculated linear operating range size (from theory) and the approximated linear operating size (from Eq. (12)) across the four dependent parameters.
Longer whiskers, and those with the sensor placed further from the base, possessed a point of most accuracy closer towards the base. However, as with the size of the operating range, the effect of the whisker length was marginal. Increasing the whisker’s momentum caused the point of most accuracy to move closer to the whisker tip. As the whisker’s centre of mass moved relatively closer to the base, so did the inflection point. clcℎar

indicated that the point of most accuracy was closer to the base for T2D whiskers than T1D whiskers. l

∗
cℎar was
practically unchanged with the presence of a medulla.

### 3.2. Effect of whisker properties

Fig. 5 shows the change in contact localisation performance as a measure of the operating range W for equivalent T1D and T2D whiskers with length lw = 200 mm, sensor location l

s = 20 mm (0.1lw), and
momentum factor wb × vc = 1 mm²/s, as the taper deviated from T

∗
This shows that the shape of the whisker drives contact localisation performance, with optimally tapered T2D whiskers naturally possessing a larger operating range than equivalent optimised T1D whiskers. A rapid reduction in W was observed for T < T ∗
, which eventually
decayed to zero. The rate of decay was greater for the T1D whisker. For T > T ∗

, W ∗ decreased gradually towards an asymptote. This rate of decay was equal for both T1D and T2D whiskers. Essentially, deviation of the whisker taper from the optimal was detrimental to the whisker performance, but increasing the whisker taper above the optimal (i.e., more taper) was less detrimental than decreasing the taper from optimal.
Fig. 6 shows the change in whisker performance as a measure of W as a result of deviating from T

∗
for T2D whiskers across varying whisker lengths (Fig. 6(a)), varying sensor locations (Fig. 6(b)), and varying momentum factors (Fig. 6(c)). Refer to Fig. E.1 in Appendix E for this relationship for T1D tapers.

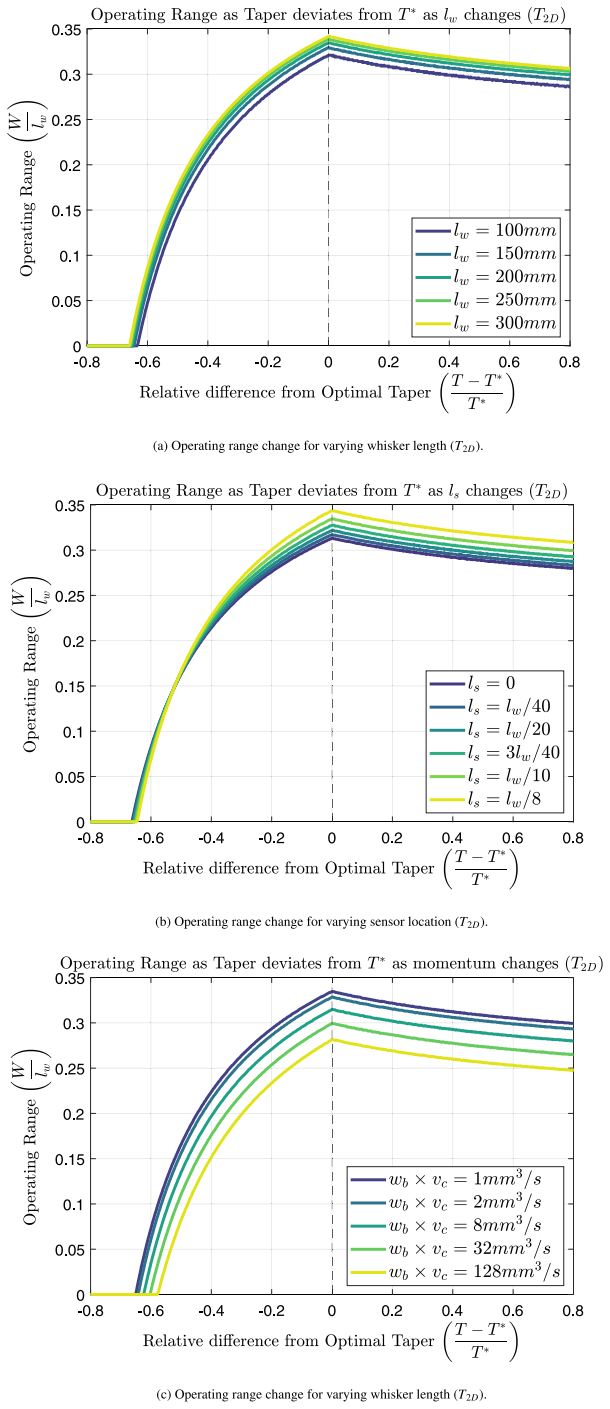
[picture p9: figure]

Fig. 6. Operating range width for T2D whiskers as the taper deviates from optimal for (a) varying whisker length (l

s = 0.1lw, wb × vc = 1), (b) varying sensor location (lw = 200 mm, wb ×vc = 1), and (c) varying momentum factor (lw = 200 mm, l
s = 0.1lw).

Longer whiskers, whiskers with sensors placed further from the base, and those with less momentum experienced a faster reduction in performance than the contrary as the taper was reduced from the

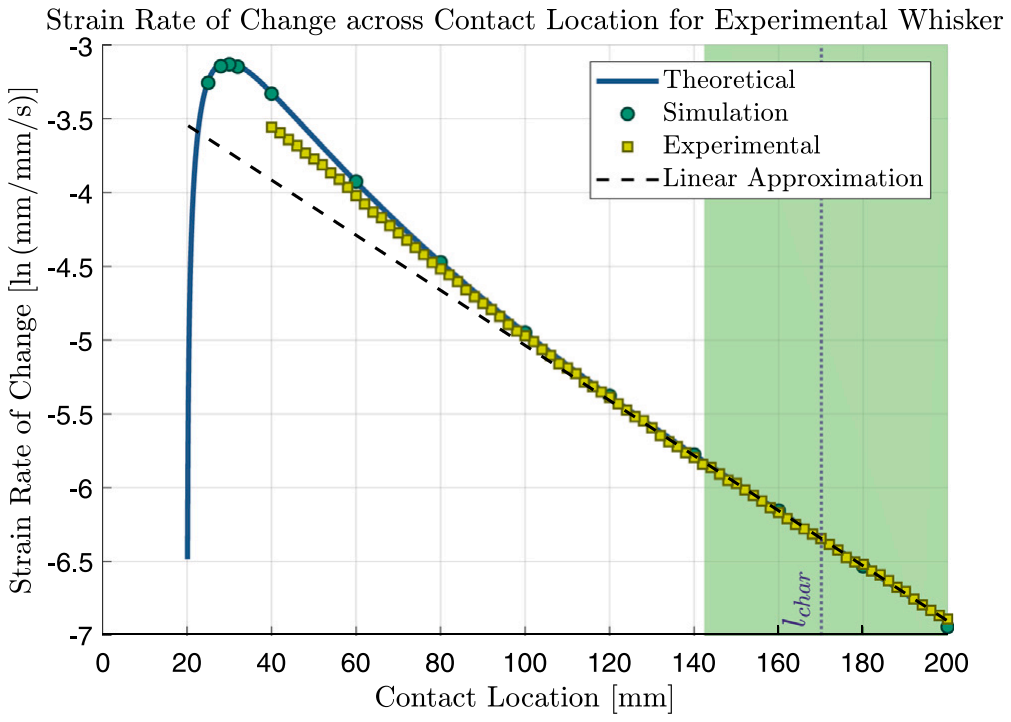
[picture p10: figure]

Fig. 7. Strain rate of change across contact location for the experimental whisker. The solid line represents the theoretical strain rate of change curve for the whisker calculated using Eq. (8b), circle datapoints show the results from the simulations, and square datapoints show the experimental results measured using the analysis window. The dotted vertical line at x = 170 mm represents the location of the whisker’s characteristic inflection point. The shaded vertical area (143 mm leq x ≤200 mm) represents the linear operating range of the whisker based on Eq. (11). The dashed line represents the linear approximation of the strain rate of change centred at the inflection point.

optimal (T < T ∗
). The rate of decay was equivalent for T1D and T2D whiskers as taper increased from optimal (T > T ∗
), and did not
change across whisker length, sensor location or momentum factor. The whisker performance was superior for longer whiskers and for those with minimal momentum. Whiskers with sensors placed further towards the tip also showed superior performance, except for cases in which the relative difference from the optimal taper fell below −0.52 for which the inverse was true.
Simulation results for whiskers made from different materials, but having the same geometry, showed that there was no difference in the strain rate of change of the whisker for a given translational deflection rate of change at equivalent contact locations.

### 3.3. Performance of an electromechanical whisker with optimal taper

To demonstrate the utility of this approach, parameters that were practically useful for a small ground robot operating in confined, cluttered spaces were selected. The parameters used were a length of lw=200 mm to enable object avoidance without reliance on LiDAR, sensor location of l

s=20 mm to increase the total operating range, base width of wb=4.5 mm for maximum achievable flexibility based on the strain gauge dimensions, and a contact speed of vc=16 mm/s to maximise the strain rate of change response with the motorised linear rail. Based on Eq. (10b), T

∗
2D

=8.84 for this whisker system. From Eqs. (11) and (12), the size of operating range was approximately

### 58 mm (0.283lw), ranging between 143 mm ≤ l

c ≤ 200 mm, with
the characteristic inflection point located at 173 mm (0.864lw). Following 3D printing, the experimental whisker used was measured to have a taper of T2D=9.0 (wb=4.5 mm and wt=1.5 mm), i.e., slightly larger than the theoretical optimal. However, the printed whisker had an estimated operating range of only 0.1 mm (0.001lw) smaller than optimal. The characteristic inflection point was located at l

cℎar=170 mm, a 3 mm shift towards the base compared to the theoretical optimal.
The specific equation for the strain rate of change due to contact location for the experimental whisker was therefore given by Eq. (13):

̇εsT2D

(l
c

) =

0.664(l

c − 20)(200 − 0.67l
c

)

l
c

, {20 mm ≤ l

c ≤ 200 mm} (13)

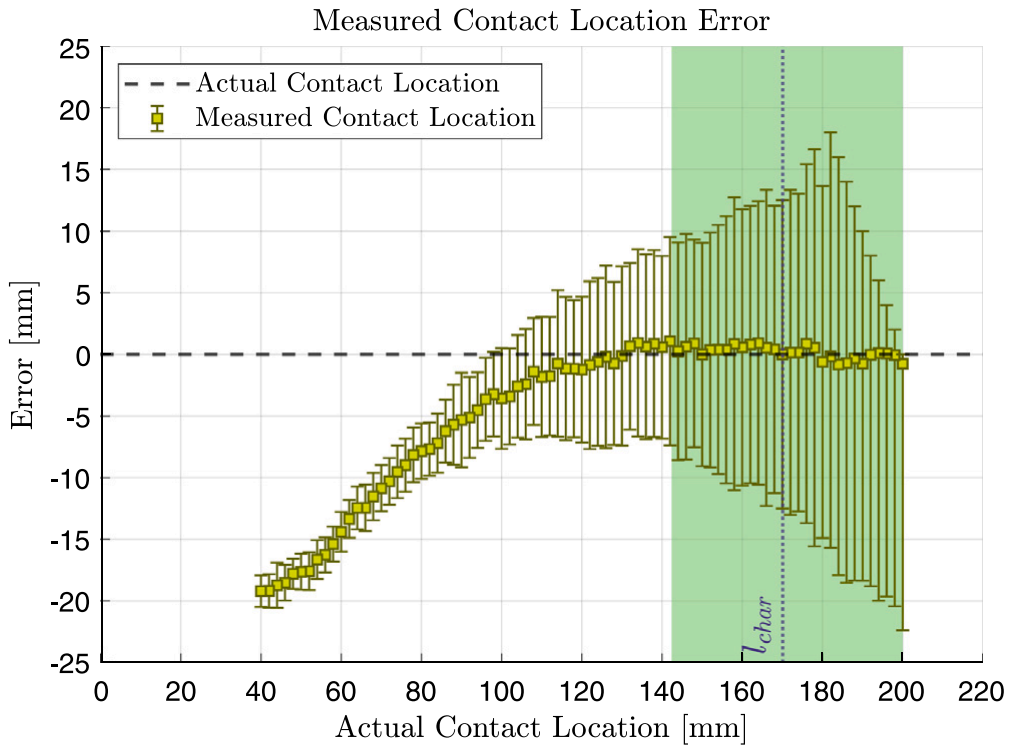
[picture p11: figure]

Fig. 8. Error between the measured contact location using the inverse linear approximation model and the actual contact location across the whisker length. Data points represent the average value, and error bars were ±2σ of the measurements within the analysis window (0.1 s). The dotted vertical line at x = 170 mm represents the location of the whisker’s characteristic inflection point. The shaded vertical area (143 mm leq x ≤200 mm) represents the linear operating range of the whisker based on Eq. (11).

The specific linear approximation for the experimental whisker was given by Eq. (14):

̂̇εsT2D
(l
c

) = exp (
−0.0187l

c − 3.17)
, | {143 mm ≤ l
c ≤ 200 mm} | (14)

Fig. 7 compares the measured rate of change of the whisker strain across contact location from the experimental whisker to that from simulations, theoretical calculations and the derived linear approximation. The simulation results showed an almost perfect correlation with the theoretical model, returning an average R² value of 0.99 and RMSE of 0.00034. This indicated that the derived theoretical model, and therefore the ascertained effect of the whisker’s properties as described in Section 3.2, hold true.
The experimental results followed the shape of the theoretical strain rate of change and contact location relationship closely for the majority of the whisker length, returning an R² value of 0.95 and RMSE of 0.0017 for all tested contact locations. Within the linear operating range, the R² value improved to 0.998 with RMSE of 0.000025, whereas outside of the linear operating range the R² value was 0.92 with RMSE of 0.0021. This indicated that the relationship between strain rate of change and contact location could be accurately predicted within the specified operating range when using the linear approximation model, with increasing error as the contact location moved further outside of the operating range.
Fig. 8 shows the difference between the measured contact location using the inverse of the linear approximation model and the actual location of the contact during the experiment, i.e., the error. Data points represent the measured contact location using the analysis window, and error bars represent two standard deviations of the measurements using the low-pass filter. Contact location measurements were clamped at a maximum of 200 mm (length of the whisker). As a result of this clamping, the error for some contacts made near to the whisker tip was asymmetrical as the positive error was restricted to the difference between the prediction using the analysis window and the whisker length. The difference between the actual contact location and the measured contact location within the analysis window was 0.19 ± 0.55 mm for contacts within the linear operating range. This was equivalent to 0.095% error, matching the defined 0.1% error limit for the operating range. The absolute error increased with an increasing rate of change as the contact location moved out of the linear operating range. For this range, the average error and standard deviation was −7.17 ± 6.65 mm.

The largest error occurred at the lowest contact location of 40 mm where the error was −19.2 mm. The error within the analysis window decreased as the contact location moved closer to the whisker base due to the increasing rate of change of the strain rate of change as the contact location approached the base.

### 4. Discussion

This research shows that a sufficient magnitude of taper is required for accurate 2D contact localisation to be achievable using a linear approximation of the whisker’s strain rate of change. This is the smallest taper for which the size of the operating range (W ) is greater than zero, which is always greater than 1 (meaning the whisker has a smaller tip than base, i.e., it is tapered) for all whiskers of realistic properties. This can be observed as the x-intercept in the examples given in Fig. 6. This follows the findings of [40] which showed that contact localisation is more accurate for tapered whiskers than untapered whiskers. This is despite the different sensing method used in this work, which points towards tapered whiskers universally providing greater accuracy than untapered whiskers. This was also observed in [30], where untapered whiskers returned lower contact localisation accuracy than tapered whiskers once the whisker deflection increased beyond 5◦
. The shape of
the whisker was also noted to be of importance for contact localisation accuracy, with T2D whiskers performing better than T1D whiskers of equivalent specifications, as observed in Fig. 5.
Our results expand on this by quantifying the taper magnitude that provides optimal performance (T

∗
) defined by having the widest operating range including the whisker tip through Eq. (10). In realistic scenarios (e.g., whisker lengths below 10s of metres, base widths in the order of mm and contact speeds in the order of mm/s to m/s), T

∗
is always smaller than infinity (i.e., the whisker never tapers to a point where wt=0), indicating that whiskers are best modelled as truncated prisms. This is also seen as the performance decays as T → +∞ (see Fig. 6). This is in agreement with the common approach of approximating rat whiskers as truncated cones [53,54]. However, as W does not approach 0 for any T > T ∗
, whiskers tapered to a point are still practical solutions, albeit sub-optimal when using our linearised signal processing approach.
Thicker whiskers require smaller tapers than thinner whiskers for optimal performance according to Eq. (10). This correlates with the geometric properties of real rat whiskers, where the longer, thicker, caudal whiskers are tapered less than the shorter, thinner, rostral whiskers [21].
An optimally tapered whisker’s point of most accuracy (the characteristic inflection point), l

∗
cℎar, was found to move towards the whisker tip as the whisker’s momentum increases (see Eq. (12)). As the momentum is proportional to wb and vc

, this implies that for a whisker of given physical properties, the point at which contact locations can be most accurately discriminated shifts with the whisk speed. This quantifies the previously suggested ‘‘sweet spot’’ between whisk speed and contact location in [52]. From a practical perspective, this implies that for applications where the contact location can be controlled, contacts should be made at the whisker’s characteristic inflection point, which requires a constant, appropriate whisk speed. This is reflective of rat behaviour, where they are observed to favour contacts near or at the whisker tip during exploration [24].
Whiskers of a given length, base width, and sensor location perform optimally at similar taper magnitudes regardless of whether or not they possess a biologically mimetic medulla. However, considering two optimally-tapered whiskers, one with a medulla and one without, the lower mass of the whisker possessing the medulla reduces sagging under gravity, the energy required to perform whisking, and the bending stiffness [20]. This ensures correlation with the derived strain rate of change to contact location relationship, reduces power consumption, and enhances mobility in confined spaces. However, due to the lowered stiffness at the base, the resolution of the whisker would decrease [20]. Therefore, in robotic mapping scenarios, it would be optimal for electromechanical whiskers to possess a medulla as long as the required sensitivity is achievable and the manufacturing process was sufficiently precise so as to not compromise the structural integrity of the whisker.

### 5. Conclusion

This paper quantified the optimal balance between the geometry, design and control of an electromechanical whisker for achieving accurate and efficient localisation of radial, translational contacts, along with their distinct effects. The use of a whisker’s optimal taper (dependent upon whisker’s length, base width, distance of the sensor from the base, and contacting speed, but independent from the presence of a biologically mimetic medulla and the whiskers material) enables the largest region of the whisker length, including the tip, to be capable of accurately localising contacts. The use of an optimally tapered whisker based on this can enhance whisker-based robotic mapping applications in terms of object localisation accuracy, whilst utilising the whisker’s entire length. Whiskers tapered in 2D are able to accurately localise contacts over a larger portion of the whisker than those tapered in 1D. This was also true for longer whiskers and those with less basal momentum (i.e., smaller cross-sections and/or slower whisk speeds). Additionally, whiskers with the strain sensing element positioned further from the base showed better performance in most cases. The developed theorem returns a characteristic contact location that results in zero error for a whisker, which is also dependent on the aforementioned whisker characteristics. This can be useful in applications requiring a controlled contact location.
These theorems are only valid for contacts occurring in a single plane and for translational whisker motion, and future work is required to quantify the relationship of whisker geometry on performance for both 3D contacts and for angular whisking behaviour. Only medullae of proportions fixed to mimic the proportions of rat whisker medullae were explored, and the impact of medullae of different proportions and shapes on the whisker performance should be analysed as this is potential grounds for further optimisation of electromechanical whisker design. The impact of the whisker dynamics on the contact localisation performance has not been explored in this research, with the whisker contact treated under static conditions. It is expected that, during translational whisker movement additional oscillatory noise would arise in the strain signal, which would reduce the precision of contact localisation. We can hypothesise that increasing the damping parameter of the whisker (e.g., by making it thicker or manufacturing it from a stiffer material) or increasing the time constant of the low-pass filter would account for this at the cost of flexibility and time to discriminate contacts, but the quantification of this should be grounds for future work.
The ensuing goal is to extend this research to the domain of measuring an object’s movability through the use of whiskers of here-derived optimal tapers by using contacts located at the characteristic contact location.

Funding

Simon P. Pegoli was supported by an Australian Government Research Training Program Scholarship.

CRediT authorship contribution statement

Simon P. Pegoli: Writing – original draft, Visualization, Validation, Software, Resources, Methodology, Investigation, Formal analysis, Data curation, Conceptualization. Phillip S.M. Skelton: Writing – review & editing, Validation, Supervision, Methodology, Conceptualization. Russell S.A. Brinkworth: Writing – review & editing, Validation, Supervision, Resources, Project administration, Methodology, Funding acquisition, Conceptualization.

Declaration of competing interest

The authors declare that they have no known competing financial interests or personal relationships that could have appeared to influence the work reported in this paper.

Data availability

Data will be made available on request.

Appendix A

A.1. Derivation of scale of diversion of second moment of area for T1D whiskers possessing a medulla

For a T1D whisker with base width wb and length lw possessing a medulla of square basal cross-section with width wm, the second moment of area at the whisker base (Imb
) is:

Imb

=

wb

4 − wm

4
12

(A.1)

Substituting Eq. (9a) into Eq. (A.1), Imb

becomes:

Imb

=

wb

4 −

(
0.324wb

)4

12

(A.2)

As the height of the whisker and the height of the medulla remain constant throughout its length, the second moment of area at the sensor location l
s

(Ims

) is:

Ims

=

wbws

3 − wmwms

3

12

(A.3)

Substituting Eqs. (3a), (9a) and (9c) into Eq. (A.3), Ims

becomes:

Ims

=

wb

(
wb

(
1 + ls
lw

(1∕T − 1)

))3
− 0.324wb

(
wb

(
0.324 − 0.415 ls
lw

))3

12
(A.4)

The scale of diversion of the second moment of area at the sensor location from that at the whisker base is therefore:

∇Im =

Ims

Imb

= 1.011 ((

1 +

l
s
lw

(1∕T − 1)

)3

− 0.324 (
0.324 − 0.415

l
s
lw

)3

)

(A.5)

Taking the ratio of ∇Im to ∇IT1D

(from Eq. (4a)):

∇Im
∇IT1D

= 1.011 −

0.324 (
0.324 − 0.415 ls
lw

)3
(
1 + ls
lw

(1∕T − 1))3

,

T ≥ 1
0 ≤ l

s∕lw ≤ 0.125

(A.6)

Substituting T = ∞ and ls∕lw = 0 into Eq. (A.6) provides the lower limit of ∇Im

∇IT1D

:

min

∇Im
∇IT1D

= 1.011 − 0.324 (0.324 − 0.415 × 0)

3

(1 + 0(1∕∞ − 1))

3

= 1.011 − 0.324⁴ = 0.99

(A.7)

Substituting T = 1 and ls∕lw = 0.125 provides the upper limit of ∇Im

∇IT1D

:

max

∇Im
∇IT1D

= 1.011 − 0.324 (0.324 − 0.415 × 0.125)

3

(1 + 0.125(1∕1 − 1))

3

= 1.004 | (A.8)

Therefore, 0.99 ≤

∇Im

∇IT1D

≤ 1.004, so ∇Im ≊ ∇IT1D

A.2. Derivation of scale of diversion of second moment of area for T2D whiskers possessing a medulla

For a T2D whisker with base width wb and length lw possessing a medulla of circular basal cross-section with width wm, the second moment of area at the whisker base (Imb
) is:

Imb

=

π
4

((wb

2

)4
−

(wm

2

)4

)
(A.9)

Substituting Eq. (9a) into Eq. (A.9), Imb

becomes:

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
0.324wb
2

)4

)

(A.10)

As both the height of the whisker and the height of the medulla taper linearly throughout its length (at different rates), the second moment of area at the sensor location l
s

(Ims

) is:

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
(wms

2

)4

)

(A.11)

Substituting Eqs. (3b), (9a) and (9c) into Eq. (A.11), Ims

becomes:

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
1 + ls
lw

(√

1∕T − 1))

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
0.324 − 0.415 ls
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
(A.12)

The scale of diversion of the second moment of area at the sensor location from that at the whisker base is therefore:

∇Im =

Ims

Imb

= 1.011 ((

1 +

l
s
lw

(√

1∕T − 1))4
−

(
0.324 − 0.415

l
s
lw

)4

)

(A.13)

Taking the ratio of ∇Im to ∇IT2D

(from Eq. (4b)):

∇Im
∇IT2D

= 1.011 −

(
0.324 − 0.415 ls
lw

)4
(
1 + ls
lw

(1∕T − 1))4

,

T ≥ 1
0 ≤ l

s∕lw ≤ 0.125 (A.14)

Substituting T = ∞ and ls∕lw = 0 into Eq. (A.14) provides the lower limit of ∇Im

∇IT2D

:

min

∇Im
∇IT2D

= 1.011 − (0.324 − 0.415 × 0)

4

(1 + 0(1∕∞ − 1))

4

= 1.011 − 0.324⁴ = 0.99 (A.15)

Substituting T = 1 and ls∕lw = 0.125 provides the upper limit of ∇Im

∇IT2D

:

max

∇Im
∇IT2D

= 1.011 − (0.324 − 0.415 × 0.125)

4

(1 + 0.125(1∕1 − 1))

4

= 1.006 | (A.16)

Therefore, 0.99 ≤

∇Im

∇IT2D

≤ 1.006, so ∇Im ≊ ∇IT2D

Appendix B

See Figs. B.1 and B.2.

Appendix C

See Figs. C.1 and C.2.

Appendix D

See Figs. D.1 and D.2.

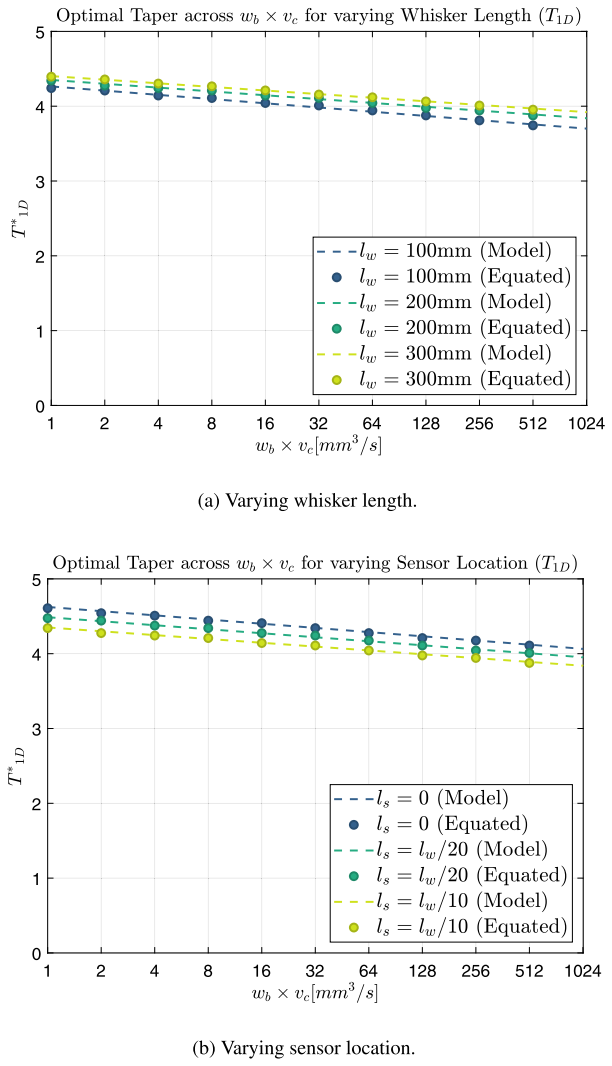
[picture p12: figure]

Fig. B.1. Optimal taper magnitude for T1D whiskers across the momentum factor for (a) varying whisker length (l

s = lw∕10), and (b) varying sensor location (lw = 200 mm). Datapoints show the optimal taper calculated directly from the theory for the respectively labelled parameter values. Dashed lines show the line of best fit from Eq. (10a) for the respectively labelled parameter values.

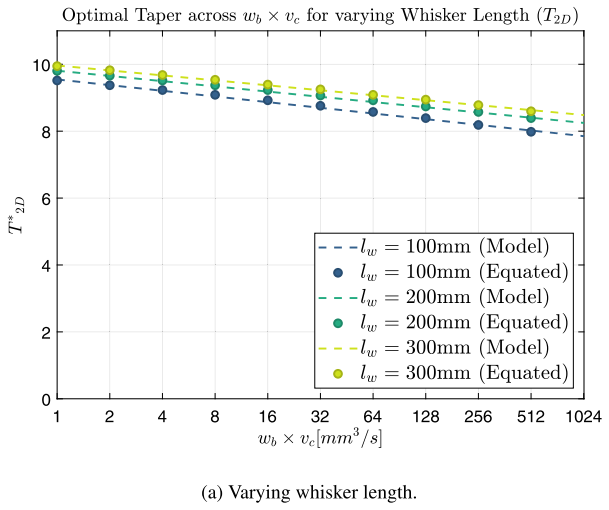
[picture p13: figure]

Fig. B.2. Optimal taper magnitude for T2D whiskers across the momentum factor for (a) varying whisker length (l

s = lw∕10), and (b) varying sensor location (lw = 200 mm). Datapoints show the optimal taper calculated directly from the theory for the respectively labelled parameter values. Dashed lines show the line of best fit from Eq. (10b) for the respectively labelled parameter values.

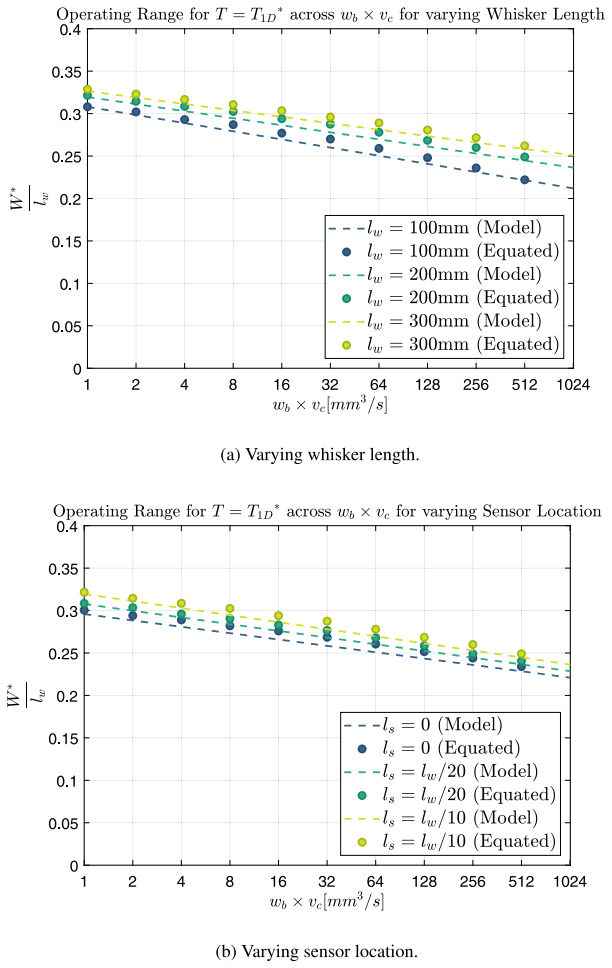
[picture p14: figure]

Fig. C.1. Size of the linear operating range for T1D whiskers with optimal taper across the momentum factor for (a) varying whisker length (l

s = lw∕10), and (b) varying sensor location (lw = 200 mm). Datapoints show the linear operating range size calculated directly from the theory for the respectively labelled parameter values. Dashed lines show the line of best fit from Eq. (11) for the respectively labelled parameter values.

Fig. C.2. Size of the linear operating range for T2D whiskers with optimal taper across the momentum factor for (a) varying whisker length (l

s = lw∕10), and (b) varying sensor location (lw = 200 mm). Datapoints show the linear operating range size calculated directly from the theory for the respectively labelled parameter values. Dashed lines show the line of best fit from Eq. (11) for the respectively labelled parameter values.

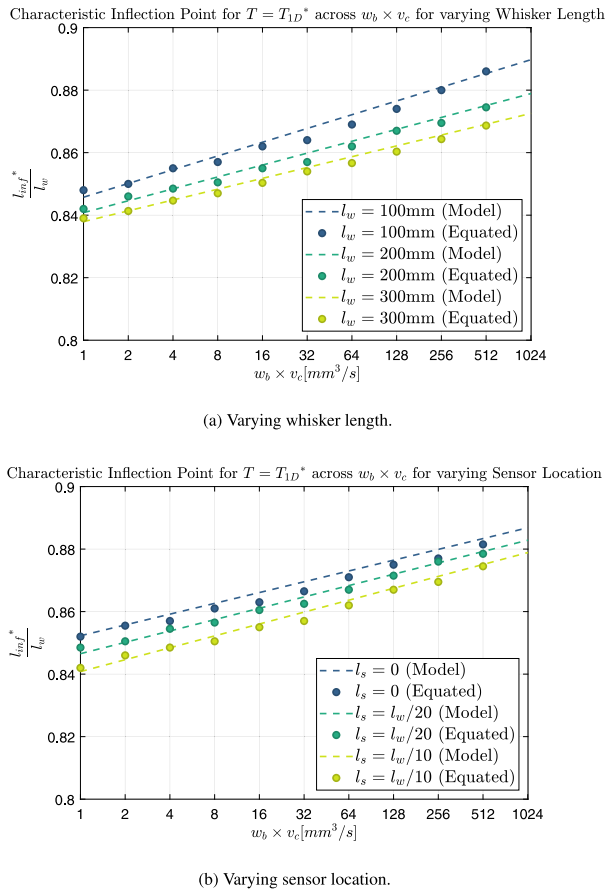
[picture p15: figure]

Fig. D.1. Location of the characteristic inflection point as a ratio of the whisker length for T1D whiskers with optimal taper across the momentum factor for (a) varying whisker length (l

s = lw∕10), and (b) varying sensor location (lw = 200 mm). Datapoints show the characteristic inflection point location calculated directly from the theory for the respectively labelled parameter values. Dashed lines show the line of best fit from Eq. (12) for the respectively labelled parameter values.

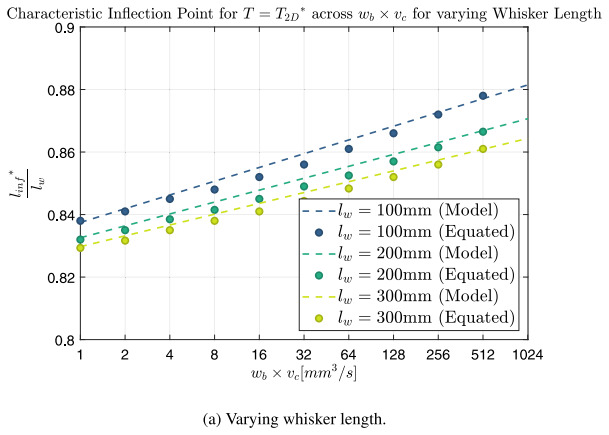
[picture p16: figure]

Fig. D.2. Location of the characteristic inflection point as a ratio of the whisker length for T2D whiskers with optimal taper across the momentum factor for (a) varying whisker length (l

s = lw∕10), and (b) varying sensor location (lw = 200 mm). Datapoints show the characteristic inflection point location calculated directly from the theory for the respectively labelled parameter values. Dashed lines show the line of best fit from Eq. (12) for the respectively labelled parameter values.

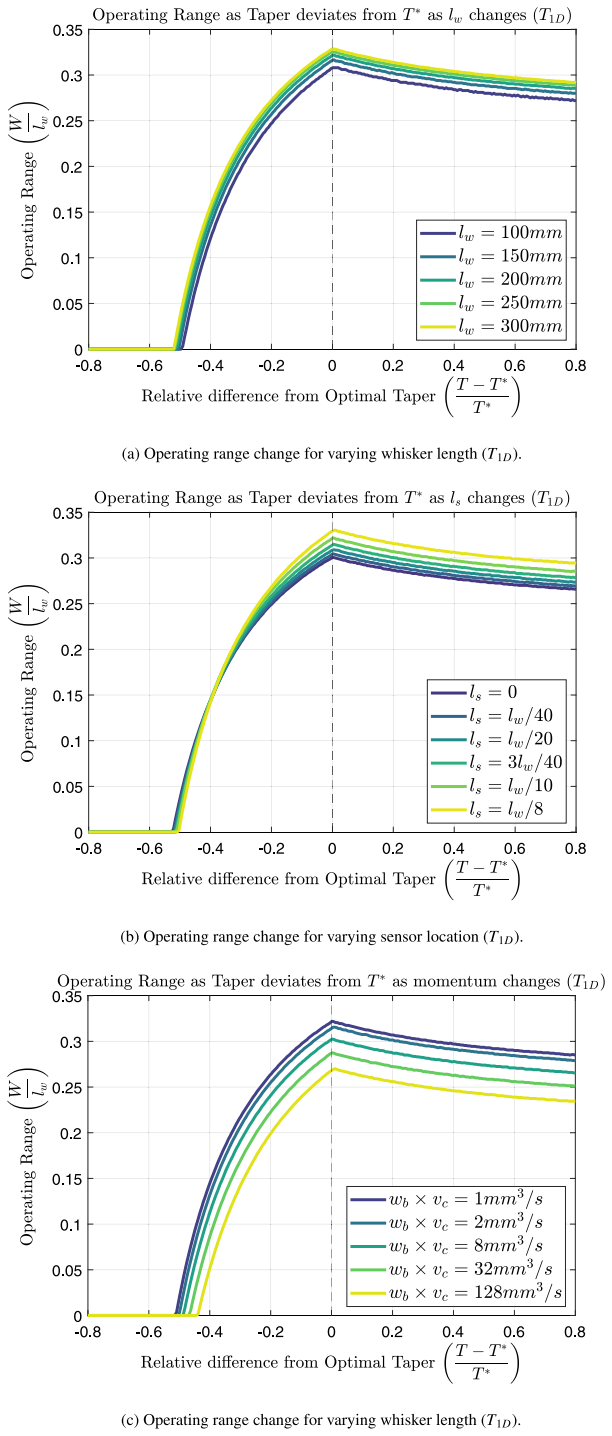
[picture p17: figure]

Fig. E.1. Operating range size for T1D whiskers as the taper deviates from optimal for (a) varying whisker length (l

s = 0.1lw, wb × vc = 1), (b) varying sensor location (lw = 200 mm, wb ×vc = 1), and (c) varying momentum factor (lw = 200 mm, l
s = 0.1lw).

Appendix E

See Fig. E.1.

References

[1] T. Buratowski, J. Garus, M. Giergiel, A. Kudriashov, Real-time 3D mapping in isolated industrial terrain with use of mobile robotic vehicle, Electronics 11 (2022) 2086, http://dx.doi.org/10.3390/electronics11132086.
[2] J.P. Queralta, J. Taipalmaa, B.C. Pullinen, V.K. Sarker, T.N. Gia, H. Tenhunen,
M. Gabbouj, J. Raitoharju, T. Westerlund, Collaborative multi-robot search and rescue: Planning, coordination, perception, and active vision, IEEE Access 8 (2020) 191617–191643, http://dx.doi.org/10.1109/ACCESS.2020.3030190.
[3] G.S. Hornby, S. Takamura, J. Yokono, O. Hanagata, T. Yamamoto, M. Fujita, Evolving robust gaits with AIBO, in: Proceedings Proceedings 2000 ICRA, San Francisco, CA, USA, 2000, http://dx.doi.org/10.1109/ROBOT.2000.846489.
[4] J.L. Jones, Robots at the tipping point: the road to iRobot Roomba, IEEE Robot. Autom. Mag. 13 (2006) 76–78, http://dx.doi.org/10.1109/MRA.2006.1598056.
[5] H. Durrant-Whyte, T. Bailey, Simultaneous localization and mapping: Part I, IEEE Robot. Autom. Mag. 13 (2006) 99–110, http://dx.doi.org/10.1109/MRA.2006. 1638022. (http://dx.doi.org/10.1109/MRA.2006.1638022)
[6] I. Lluvia, E. Lazkano, A. Ansuategi, Active mapping and robot exploration: A survey, Sensors 21 (2021) 2445, http://dx.doi.org/10.3390/s21072445.
[7] C. Rosales, F. Spinelli, M. Gabiccini, C. Zito, J.L. Wyatt, GPAtlasRRT: A local tactile exploration planner for recovering the shape of novel objects, Int. J. Humanoid Robot. 15 (2018) 1850014-1–1850014-27, http://dx.doi.org/10.1142/S0219843618500147. (http://dx.doi.org/10.1142/S0219843618500147)
[8] K.A. Nichols, A.M. Okamura, Active multiobject exploration and recognition via tactile whiskers, IEEE Trans. Robot. 38 (2022) 3479–3497, http://dx.doi.org/10.1109/TRO.2022.3182487. (http://dx.doi.org/10.1109/TRO.2022.3182487)
[9] S. Jia, L. Zhang, V.J. Santos, Autonomous tactile localization and mapping of objects buried in granular materials, IEEE Robot. Autom. Lett. 7 (2022) 9953–9960, http://dx.doi.org/10.1109/LRA.2022.3191955.
[10] Yue. Y, Y. Tang, Q. Wang, W. Xiao, J. Liu, J. Wang, M. Chen, G. Wu, B. Su, Active perception in non-visual recognition environments by stretchable tentacle sensor arrays, ACS Appl. Mater. Interfaces 14 (2022) 26913–26922, http://dx.doi.org/10.1021/acsami.2c04717.
[11] Y. Mulgaonkar, W. Liu, D. Thakur, K. Daniilidis, C.J. Taylor, V. Kumar, The tiercel: A novel autonomous micro aerial vehicle that can map the environment by flying into obstacles, in: Proceedings of the IEEE International Conference on Robotics and Automation, Paris, France, 31 May–31 August 2020, 2020, http://dx.doi.org/10.1109/ICRA40945.2020.9197269.
[12] M. Bajracharya, A. Howard, L.H. Matthies, B. Tang, M. Turmon, Autonomous off-road navigation with end-to-end learning for the LAGR program, J. Field Robotics 26 (2009) 3–25, http://dx.doi.org/10.1002/rob.20269.
[13] R.A. Grant, V.G.A. Goss, What can whiskers tell us about mammalian evolution, behaviour, and ecology? Mammal Rev. 52 (2022) 148–163, http://dx.doi.org/10.1111/mam.12253. (http://dx.doi.org/10.1111/mam.12253)
[14] R.A. Grant, V. Breakell, T.J. Prescott, Whisker touch sensing guides locomotion in small, quadrupedal mammals, Proc. R. Soc. B 285 (2018) 20180592, http: //dx.doi.org/10.1098/rspb.2018.0592.
[15] M. Brecht, B. Preilowski, M.M. Merzenich, Functional architecture of the mystacial vibrissae, Behav. Brain Res. 84 (1997) 81–97, http://dx.doi.org/10.1016/S0166-4328(97)83328-1. (http://dx.doi.org/10.1016/S0166-4328(97)83328-1)
[16] T.J. Prescott, B. Mitchinson, R.A. Grant, Vibrissal behavior and function, Scholarpedia 6 (2011) 6642, http://dx.doi.org/10.4249/scholarpedia.6642.
[17] F. Gonçalves, R.S. Bovendorp, G. Beca, C. Bello, R. Costa-Pereira, R.L. Muylaert, R.R. Rodarte, N. Villar, R. Souza, M.E. Graipel, et al., ATLANTIC MAMMAL TRAITS: a data set of morphological traits of mammals in the Atlantic Forest of South America, Ecology (2018) http://dx.doi.org/10.1002/ecy.2106.
[18] D. Voges, K. Carl, G.J. Klauer, R. Uhlig, C. Schilling, C. Behn, H. Witte, Structural characterization of the whisker system of the rat, IEEE Sens. J. 12 (2011) 332–339, http://dx.doi.org/10.1109/JSEN.2011.2161464.
[19] C.M. Williams, E.M. Kramer, The advantages of a tapered whisker, PLOS ONE 5 (2010) e8806, http://dx.doi.org/10.1371/journal.pone.0008806.
[20] A.E. Yang, H.M. Belli, M.J.Z. Hartmann, Quantification of vibrissal mechanical properties across the rat mystacial pad, J. Neurophysiol. 121 (2019) 1879–1895, http://dx.doi.org/10.1152/jn.00869.2016.
[21] H.M. Belli, A.E. Yang, C.S. Bresee, M.J.Z. Hartmann, Variations in vibrissal geometry across the rat mystacial pad: base diameter, medulla, and taper, J. Neurophysiol. 117 (2017) 1807–1820, http://dx.doi.org/10.1152/jn.00054.2016.
[22] L.A. Huet, M.J.Z. Hartmann, The search space of the rat during whisking behavior, J. Exp. Biol. 217 (2014) 3365–3376, http://dx.doi.org/10.1242/jeb. 105338. (http://dx.doi.org/10.1242/jeb.105338)
[23] G.E. Carvell, D.J. Simons, Biometric analyses of vibrissal tactile discrimination in the rat, J. Nuerosci. 10 (1990) 2638–2648, http://dx.doi.org/10.1523/JNEUROSCI.10-08-02638.1990. (http://dx.doi.org/10.1523/JNEUROSCI.10-08-02638.1990)
[24] B. Mitchinson, C.J. Martin, R.A. Grant, T.J. Prescott, Feedback control in active sensing: rat exploratory whisking is modulated by environmental contact, Proc.
R. Soc. B 274 (2007) 1035–1041, http://dx.doi.org/10.1098/rspb.2006.0347.

[25] E. Zucker, W.I. Welker, Coding of somatic sensory input by vibrissae neurons in the rat’s trigeminal ganglion, Brain Res. 12 (1969) 138–156, http://dx.doi.org/10.1016/0006-8993(69)90061-4. (http://dx.doi.org/10.1016/0006-8993(69)90061-4)
[26] M. Szwed, K. Bagdasarian, E. Ahissar, Encoding of vibrissal active touch, Neuron 40 (2003) 621–630, http://dx.doi.org/10.1016/S0896-6273(03)00671-8.
[27] E. Ahissar, P.M. Knutsen, Object localization with whiskers, Biol. Cybernet. 98 (2008) 449–458, http://dx.doi.org/10.1007/s00422-008-0214-4.
[28] L. Pammer, D.H. O’Connor, S.A. Hires, N.G. Clack, D. Huber, E.W. Myers, K. Svoboda, The mechanical variables underlying object localization along the axis of the whisker, J. Neurosci. 33 (2013) 6726–6741, http://dx.doi.org/10.1523/JNEUROSCI.4316-12.2013. (http://dx.doi.org/10.1523/JNEUROSCI.4316-12.2013)
[29] D.B. Polley, J.L. Rickert, R.D. Frostig, Whisker-based discrimination of object orientation determined with a rapid training paradigm, Neurobiol. Learn. Memory 83 (2005) 134–142, http://dx.doi.org/10.1016/j.nlm.2004.10.005.
[30] N.H. Nguyen, T.D. Ngo, D.Q. Nguyen, Contact distance estimation by a soft active whisker sensor based on morphological computation, in: 2020 8th IEEE RAS/EMBS International Conference for Biomedical Robotics and Biomechatronics (BioRob), New York, NY, USA, 2020, http://dx.doi.org/10.1109/BioRob49111.2020.9224314. (http://dx.doi.org/10.1109/BioRob49111.2020.9224314)
[31] J.H. Solomon, M.J. Hartmann, Robotic whiskers used to sense features, Nature 443 (2006) 525, http://dx.doi.org/10.1038/443525a.
[32] C. Xiao, S. Xu, W. Wu, J. Wachs, Active multiobject exploration and recognition via tactile whiskers, IEEE Trans. Robot. 38 (2022) 3479–3497, http://dx.doi.org/10.1109/TRO.2022.3182487. (http://dx.doi.org/10.1109/TRO.2022.3182487)
[33] W. Deer, P.E.I. Pounds, Lightweight whiskers for contact, pre-contact, and fluid velocity sensing, IEEE Robot. Autom. Lett. 4 (2019) 1978–1984, http://dx.doi.org/10.1109/LRA.2019.2899215. (http://dx.doi.org/10.1109/LRA.2019.2899215)
[34] Y. Zhang, S. Yan, Z. Wei, X. Chen, T. Fukuda, Q. Shi, A small-scale, rat-inspired whisker sensor for the perception of a biomimetic robot: Design, fabrication, modeling, and experimental characterization, IEEE Robot. Autom. Mag. 29 (2022) 115–126, http://dx.doi.org/10.1109/MRA.2022.3182870.
[35] C. Zhao, Q. Jiang, Y. Li, A novel biomimetic whisker technology based on fiber Bragg grating and its application, Meas. Sci. Technol. 28 (2017) 095104, http://dx.doi.org/10.1088/1361-6501/aa7d36.
[36] M.J. Pearson, B. Mitchinson, J. Welsby, T. Pipe, T.J. Prescott, Scratchbot: Active tactile sensing in a whiskered mobile robot, in: Proceedings of the International Conference on Simulation of Adaptive Behavior, Paris, 25-28 August 2010, 2010, http://dx.doi.org/10.1007/978-3-642-15193-4_9.
[37] M.A. Lin, E. Reyes, J. Bohg, M.R. Cutkosky, Whisker-inspired tactile sensing for contact localization on robot manipulators, in: Proceedings of the IEEE/RSJ International Conference on Intelligent Robots and Systems, Kyoto, Japan, 23-27 October 2022, 2022, http://dx.doi.org/10.1109/IROS47612.2022.9982122.
[38] M.A. Sayegh, H. Daraghma, S. Mekid, S. Bashmal, Review of recent bio-inspired design and manufacturing of whisker tactile sensors, Sensors 22 (2022) 2705, http://dx.doi.org/10.3390/s22072705.
[39] M. Evans, C.W. Fox, M.J. Pearson, T.J. Prescott, Spectral template based classification of robotic whisker sensor signals in a floor texture discrimination task, in: Proceedings TAROS, 2009, pp. 19–24. (http://refhub.elsevier.com/S0924-4247(24)00585-5/sb39)
[40] D.W. Collinson, H.M. Emnett, J. Ning, M.J.Z. Hartmann, L.C. Brinson, Tapered polymer whiskers to enable three-dimensional tactile feature extraction, Soft Robot. 8 (2021) 44–58, http://dx.doi.org/10.1089/soro.2019.0055.
[41] S. Mekid, H. Daraghma, Experimental ultrasonic sub-surface consolidation of fiber bragg grating for sensorial materials, J. Mater. Process. Technol. 252 (2018) 673–679, http://dx.doi.org/10.1016/j.jmatprotec.2017.10.036.
[42] S. Mekid, H. Daraghma, Sensing signal assessment in sensorial materials: Key embedding conditions, in: Proceedings of International Multi-Conference on Systems, Signals & Devices, Monastir, Tunisia, 20-23 July 2020, 2020, http: //dx.doi.org/10.1109/SSD49366.2020.9364207.
[43] C. Fox, M. Evans, M. Pearson, T.J. Prescott, Tactile SLAM with a biomimetic whiskered robot, in: Proceedings of IEEE International Conference on Robotics and Automation, Saint Paul, Minnesota, USA, 14-18 May 2012, 2012, http: //dx.doi.org/10.1109/ICRA.2012.6224813.
[44] M.J. Pearson, C. Fox, J.C. Sullivan, T.J. Prescott, T. Pipe, B. Mitchinson, Simultaneous localisation and mapping on a multi-degree of freedom biomimetic whiskered robot, in: Proceedings of the IEEE International Conference on Robotics and Automation, Karlsruhe, Germany, 6-10 May 2013, 2013, http: //dx.doi.org/10.1109/ICRA.2013.6630633.
[45] O. Struckmeier, K. Tiwari, M. Salman, M.J. Pearson, V. Kyrki, Vita-slam: A bio-inspired visuo-tactile slam for navigation while interacting with aliased environments, in: Proceedings of the IEEE International Conference on Cyborg and Bionic Systems, Munich, Germany, 19-20 September 2019, 2019, http: //dx.doi.org/10.1109/CBS46900.2019.9114526.
[46] C.W. Fox, B. Mitchinson, M.J. Pearson, A.G. Pipe, T.J. Prescott, Contact type dependency of texture classification in a whiskered mobile robot, Auton. Robots 26 (2009) 223–239, http://dx.doi.org/10.1007/s10514-009-9109-z.
[47] N.F. Lepora, M. Evans, C.W. Fox, M.E. Diamond, K. Gurney, T.J. Prescott, Naive Bayes texture classification applied to whisker data from a moving robot, in: Proceedings of the International Joint Conference on Neural Networks, Barcelona, Spain, 18-23 July 2010, 2010, http://dx.doi.org/10.1109/IJCNN.2010.5596360.
[48] H. Wegiriya, N. Herzig, S.A. Abad, S.M.H. Sadati, T. Nanayakkara, A stiffness controllable multimodal whisker sensor follicle for texture comparison, IEEE Sens. J. 20 (2019) 2320–2328, http://dx.doi.org/10.1109/JSEN.2019.2951755.
[49] O.A. Bauchau, J.I.B. Craig, Structural Analysis: With Applications To Aerospace Structures, first ed., Springer Dordrecht, Berlin, Germany, 2009, pp. 173–221, http://dx.doi.org/10.1007/978-90-481-2516-6.
[50] S.A. Hires, L. Pammer, K. Svoboda, D. Golomb, Tapered whiskers are required for active tactile sensation, eLIFE 2 (2013) e01350, http://dx.doi.org/10.7554/eLife.01350. (http://dx.doi.org/10.7554/eLife.01350)
[51] L.A. Huet, J.W. Rudnicki, M.J.Z. Hartmann, Tactile sensing with whiskers of various shapes: Determining the three-dimensional location of object contact based on mechanical signals at the whisker base, Soft Robot. 4 (2017) 88–102, http://dx.doi.org/10.1089/soro.2016.0028.
[52] M.H. Evans, C.W. Fox, M.J. Pearson, T.J. Prescott, Tactile discrimination using template classifiers: Towards a model of feature extraction in mammalian vibrissal systems, in: Proceedings of the International Conference on Simulation of Adaptive Behavior, Paris, France, 25-28 August 2010, 2010, http://dx.doi.org/10.1007/978-3-642-15193-4_17. (http://dx.doi.org/10.1007/978-3-642-15193-4_17)
[53] M.J. Hartmann, N.J. Johnson, R.B. Towal, C. Assad, Mechanical characteristics of rat vibrissae: resonant frequencies and damping in isolated whiskers and in the awake behaving animal, J. Neurosci. 23 (2003) 6510–6519, http://dx.doi.org/10.1523/JNEUROSCI.23-16-06510.2003. (http://dx.doi.org/10.1523/JNEUROSCI.23-16-06510.2003)
[54] J.A. Birdwell, J.H. Solomon, M. Thajchayapong, M.A. Taylor, M. Cheely, R.B. Towal, J. Conradt, M.J.Z. Hartmann, Biomechanical models for radial distance determination by the rat vibrissal system, J. Neurophysiol. 98 (2007) 2439–2455, http://dx.doi.org/10.1152/jn.00707.2006.

Simon P. Pegoli received a B.Eng degree in Mechatronics with first class honours from the University of South Australia in 2020. He is a current Ph.D. student with the College of Science and Engineering at Flinders University, Australia. Simon’s research interests include autonomous robotic mapping and navigation using tactile sensing, specifically for confined environments containing movable and compliant objects.

Phillip S.M. Skelton was awarded his Ph.D. in biologically inspired machine vision systems by the University of South Australia in 2020. He joined Flinders University’s College of Science and Engineering in 2020 as a Post-Doctoral Research Associate, where he worked across all aspects of maritime underwater autonomous systems. His research focus was on adaptive biologically inspired signal processing algorithms for multi-modal autonomous perception tasks in the underwater domain. In 2024, Dr Skelton commenced as a Researcher at the University of South Australia, working on improving remote sensing and autonomous identification systems for Forestry applications.

Russell S. A. Brinkworth received a Ph.D. degree in neuroscience from the University of Adelaide in 2004. He joined the Insect Vision Laboratory as a Post-Doctoral Researcher then as an ARC Research Fellow. Becoming a Lecturer in mechanical engineering in 2010. He moved to the University of South Australia as the Program Director for Autonomous Systems in 2011. In late 2019, he joined the College of Science and Engineering at Flinders University as an Associate Professor of Autonomous Systems. Russell’s primary research interest is in combining neuroscience and signal processing concepts and techniques within the sensor systems of autonomous platforms.

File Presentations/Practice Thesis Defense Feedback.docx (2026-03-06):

Tania
Great first pass!! Overall, a little long -- so we should think about where to cut a bit (5-8 min or so? since need to add in conclusion still) too:

- Let's discuss title ideas a little bit! I think what you have so far is good, but let's just finalize
- Can we call it multi-point? Or is that too broad?
- Should we start with one slide on continuum robots, and tendon driven robots specifically?
- Slide 4: can we add some figures? --> what about a continuum robot with forces being applied at least?
  - for why force sensing? --> maybe not just for haptics, but also for controls!
- Slide 6: have to be a little careful about saying they are impractical to implement (may need to be more specific to continuum robots) since Intuitive does use this for their instruments
- Slide 9: write out which one is tapered vs cylindrical for figure on bottom left
- Slide 10: what do you mean by "turbulence"?
- Slide 13: should we change the last point to be a research question?
- Slide 16: don't need to go into too much detail on the ones you tried, but mostly focus on rationale for sorosim is good
- Slide 17: should show which is robot base vs tip
  - are the grey circles along the backbone the disks? should they have a thickness?
- Slide 18: should we show a cross section of the robot with the tendons? In particular, maybe a cross section where the backbone is elliptical?
- Slide 22: somewhere before this -- should show the setup! Not clear that you have a 6 DOF F/T sensor and load cells
- Slide 25: can you make arrows btwn "residual vector" and "forward model" blocks show exactly where the inputs/outputs are connected? (i.e. to/from R.1 right?
- Slide 31: update variable for condition number
- In optimization wokflow: What is M_init?
- Slide 38: not sure if we need the algorithm? Can we just put this info on scoring in the workflow?
- Slide 40: show which is base vs tip of robot
- Slide 41: add refs for the figures
- Slide 42: maybe just a cross sectional view instead of exploded view for A?
- Slide 44: what do you mean by "discrete" proportional tension control?
- Slide 46: again show tip vs base
- Slide 47: what is MAE?
- Slide 47: are errors based on mean? or median?
- Slide 51: can we use more representative graphics?

Questions:

- How did you decide on how many segments to optimize?
- Is two forces the maximum that it can estimate?
- Intuitively do you have an idea why the tip is so thick? (compared to tapered design in biology?)
- Should there be a tapered design to compare to?

Anna
Feedback for Noah's presentation:

- video of the optimization -- would be good to clarify how the initial conditions are found/give visuals of the gradient free process?
- no torsion assumption (what are the configuration of the TDCR in which the torsion is non trivial?) --> plot the configuration vs. expected torsion to back up your assumption
- clarify what the safety constraint enforces (constraints on minimum diameter, or on the configuration, tendon tension?) --> why can't you just set a bound on the minimum diameter directly?
- plot on slide 46: cost starting at 0 -> would be good to talk about earlier if your cost function is actually bounded?
- for the error plots -- how close are the two forces tested?

Sukjun
Motivation slide: think about dividing this into three slides with some figures or videos?

Intro seems to be a bit too long. Keeping it more concise and hitting only the important part will be helpful! On the bioinspiration slides, first part is about active whisking, the second part is the geometry, third is also assymetric geometry, forth(elephant) is also geometry. You can shorten this part and it is not necessary to show the results from previous work. If you are not doing active whisking, rat whisker part could be omitted.

Slide 17, talk about the geometry first and why you are using variable radius rod design. Where did you find inspiration for this design?

When introducing the design, you can mention that ‘ i will go through a modeling algorithm for a given design and then in the next section i will talk about how the continuum design can be optimized to maximize the accuracy if the force estimation’ or something.

Slide 44 some slides have too much information. Board or chip model doesn’t need to be presented. Of course you need them in the thesis!

My comments from today!

Karen
General Feedback & Background

- May be helpful to establish some background (relevant works, etc.) before jumping into surgical applications.
- Add specific citations for places you state things come from literature.

Slide-Specific Notes

Slide 4

- Why is multi-force localization essential?
- Wouldn't traditional navigill [navigation] instruments only essentially be giving backend info to the surgeons?

Slide 6

- Why is it bad to [be] electronic?
- Are there situations where these may have issues with surgical imaging?

Slide 8

- Is there an inherent limitation to the works that have only shown tip force estimation?
- Would the technique not work at an arbitrary location?

Slide 10

- Does the reduced turbulence in seal whiskers apply at all in air?
- Is that the only benefit of the shape?

Slide 14

- I vaguely remember you mentioning modeling your test rig after one in the literature; is it still similar or truly unique at this point?

Slide 17

- Is the deflection in each segment small enough for the linear assumption to hold?
- Is there a quantitative way to show your disks are sufficiently thin?

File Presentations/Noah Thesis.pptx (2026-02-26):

## Bioinspired Backbone Geometry for Multi-Point 3D Force Estimation in Continuum Robots

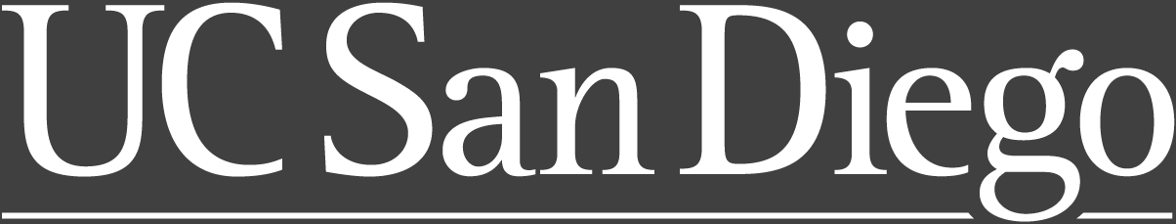
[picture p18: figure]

Noah L Jones, Anna Xu, Tania K Morimoto

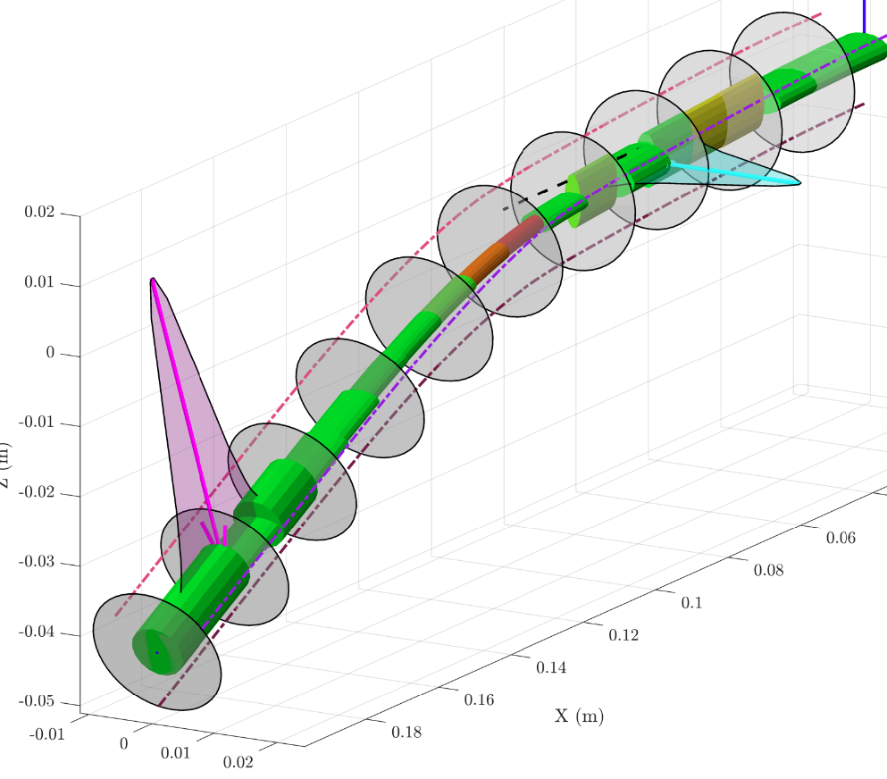
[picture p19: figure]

University Communications | October 17, 2023

## Contents

Background & Motivation

1

2

Force Estimation Model

3

Design Optimization

4

Fabrication

5

Results & Discussion

6

Conclusion & Future Work

## Introduction

## Motivation

Why Force Sensing Matters
- Haptic feedback reduces unintended tissue damage and enables precise manipulation, grasping, compliance, and autonomy¹⁻⁴
Why Whole-Body Sensing is Needed
- Surgeons must distinguish tip forces from unintended body contacts along the shaft
- Force direction identifies constraint type (sliding vs. catching)⁵
The Core Challenge
- Multi-point spatial force localization is essential yet difficult in small continuum robots⁶
Why Not Direct Sensors?
- Hard to integrate, difficult to sterilize, limited to discrete points⁷⁸

## Limitations of Current Approaches

Shape/Curvature-Based Sensing (e.g., FBGs, Vision)
- Infers forces from backbone deformation using robot models (e.g., Cosserat rod theory)¹
- FBGs can localize up to three point forces — but the inverse problem is fundamentally ill-conditioned²
- Vision-based tracking is more affordable but requires direct line-of-sight — impractical in confined surgical environments³⁻⁵

## Limitations of Current Approaches

## Limitations of Current Approaches

## Bio-Inspiration

This template was built for general use using the UC San Diego logo. For units wanting to use their unit-specific sub-brand logo, follow the steps and tips below.
- PNG files work best, as they have a transparent background.
- To update the logo on one of the cover designs, select the logo image and click Replace Image from the toolbar (or right click and choose Replace Image). To adjust the crop to fit the logo, click the Reset Image button (or right click the image and choose Reset Image).
- Content slides, like this one, can be tight on space, making it harder to fit unit sub-brand logos legibly. We recommend keeping the main UC San Diego logo on these slides. If you need to update the page header logo, click on View/Theme Builder and select the theme slide. Follow the steps above for replacing the image.

## Contributions

This template was built for general use using the UC San Diego logo. For units wanting to use their unit-specific sub-brand logo, follow the steps and tips below.
- PNG files work best, as they have a transparent background.
- To update the logo on one of the cover designs, select the logo image and click Replace Image from the toolbar (or right click and choose Replace Image). To adjust the crop to fit the logo, click the Reset Image button (or right click the image and choose Reset Image).
- Content slides, like this one, can be tight on space, making it harder to fit unit sub-brand logos legibly. We recommend keeping the main UC San Diego logo on these slides. If you need to update the page header logo, click on View/Theme Builder and select the theme slide. Follow the steps above for replacing the image.

## Force Estimation Model

## Modeling Framework

This template was built for general use using the UC San Diego logo. For units wanting to use their unit-specific sub-brand logo, follow the steps and tips below.
- PNG files work best, as they have a transparent background.
- To update the logo on one of the cover designs, select the logo image and click Replace Image from the toolbar (or right click and choose Replace Image). To adjust the crop to fit the logo, click the Reset Image button (or right click the image and choose Reset Image).
- Content slides, like this one, can be tight on space, making it harder to fit unit sub-brand logos legibly. We recommend keeping the main UC San Diego logo on these slides. If you need to update the page header logo, click on View/Theme Builder and select the theme slide. Follow the steps above for replacing the image.

## Model Configuration

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

## The Forward Model

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

## The Inverse Model

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

## Design Optimization

## The Ill-Conditioned Cylindrical Backbone

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

## Design Optimization Formulation

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

## Fabrication

## Continuum Robot Fabrication

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

## Testing Rig Fabrication

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

## Electronics

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

## Results & Discussion

## Conclusion & Future Work

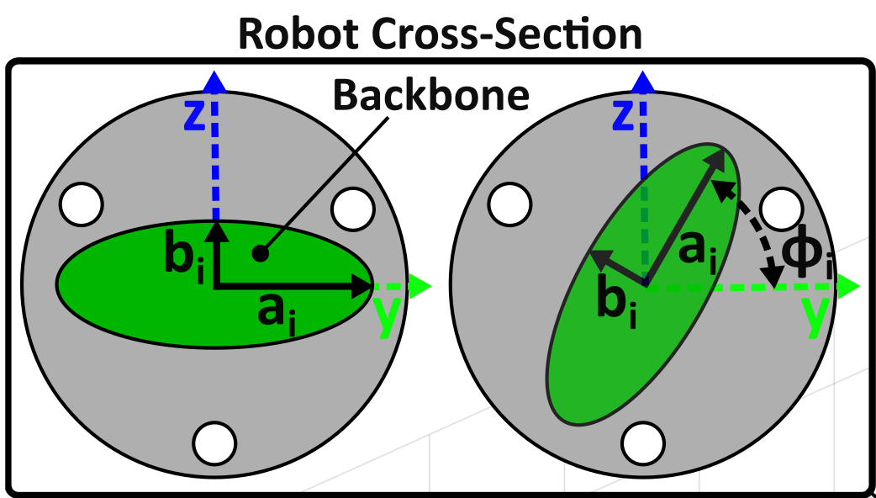
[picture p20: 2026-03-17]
Figures/Design Variables.png

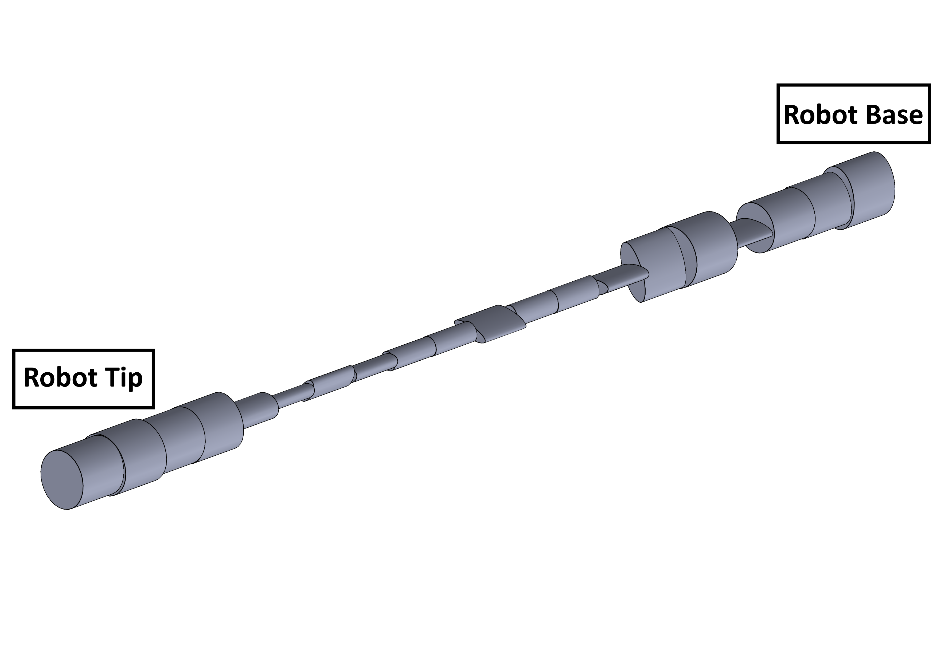
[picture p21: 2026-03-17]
Figures/Optimal Design CAD.png

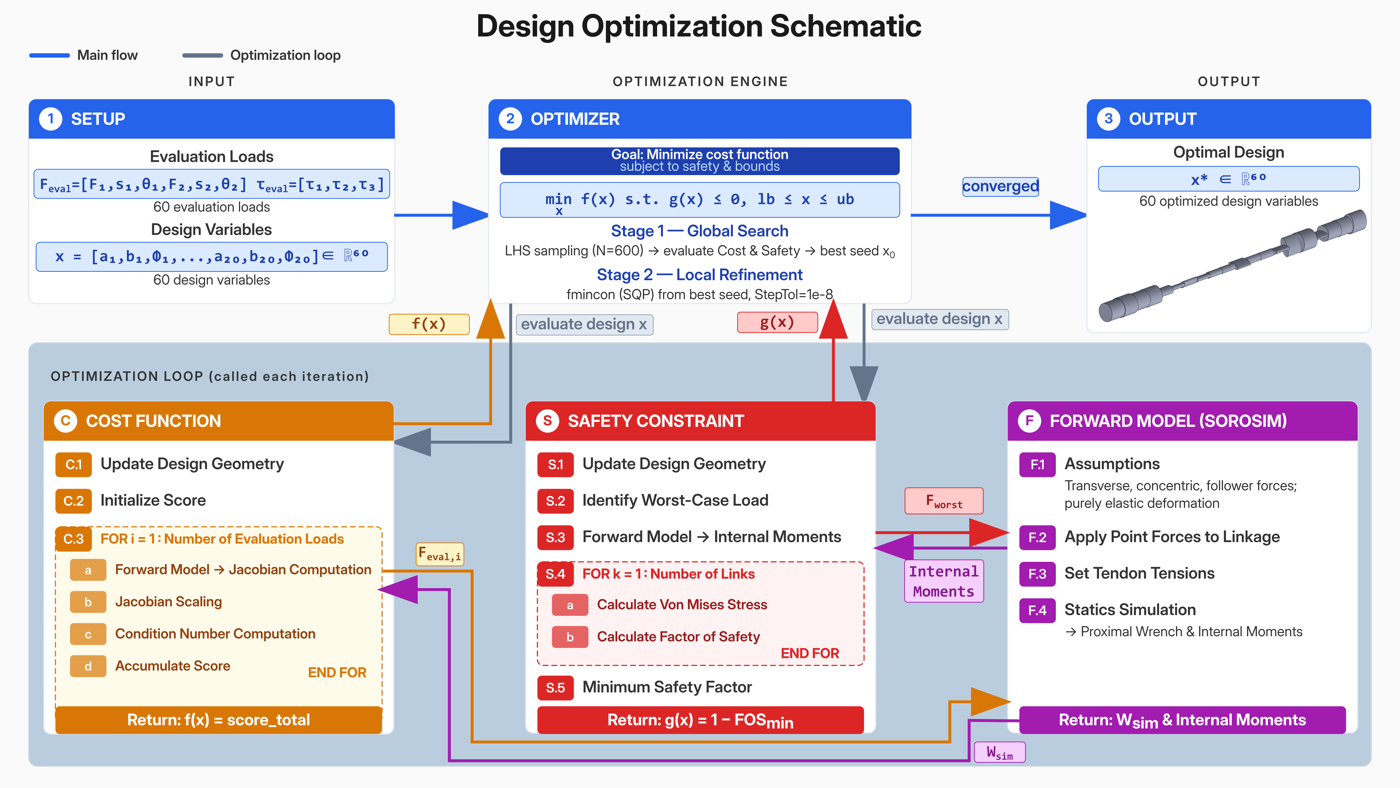
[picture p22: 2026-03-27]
Figures/High Level Design Opt.png

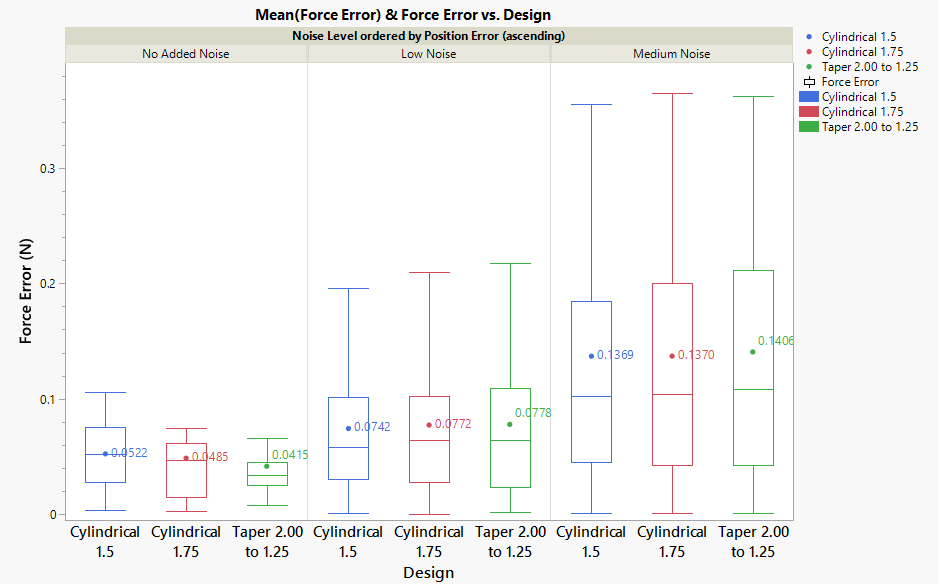
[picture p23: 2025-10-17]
Images and Videos/Force_Error_3Designs.png

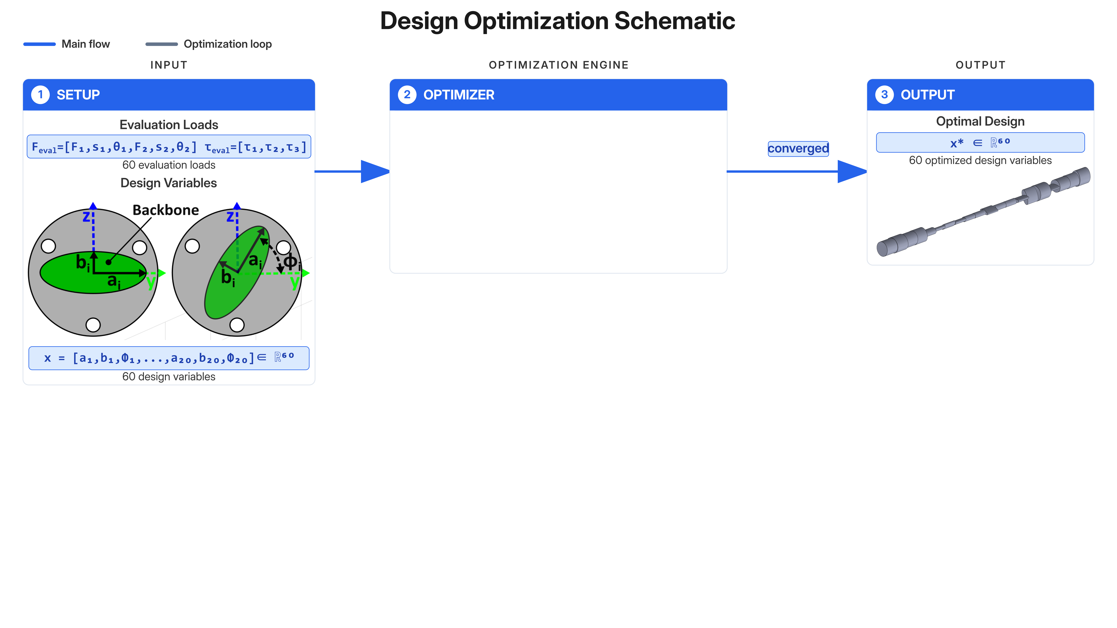
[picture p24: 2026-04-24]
Images and Videos/High Level Design Opt.png

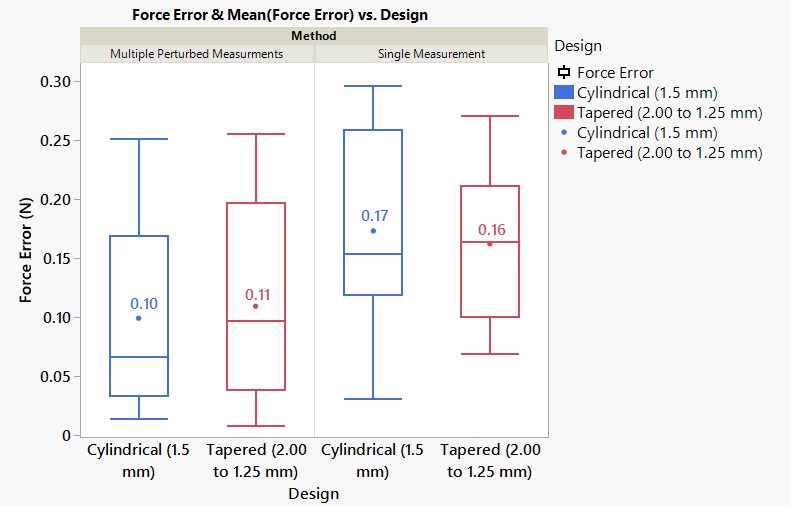
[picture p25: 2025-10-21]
Images and Videos/Sort of Custom Design by el1, s1, F1, el2, s2, F2, tau1 - 2method2design force.png

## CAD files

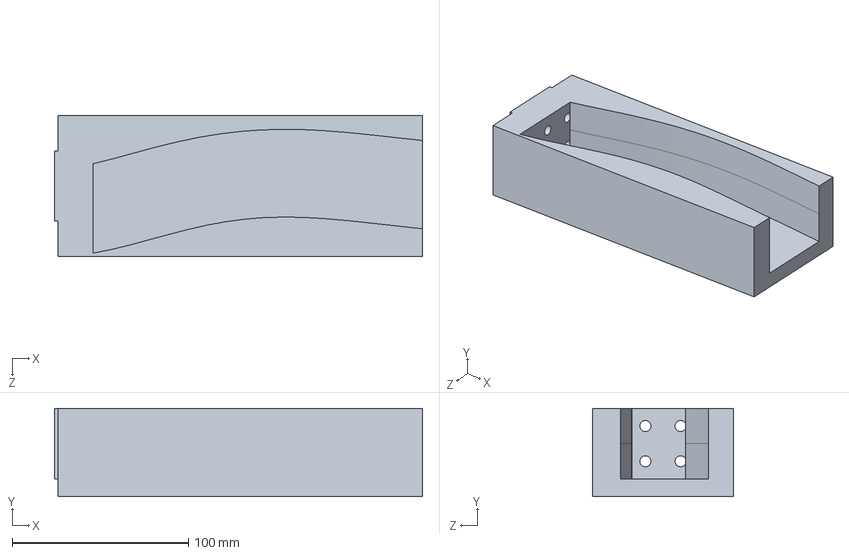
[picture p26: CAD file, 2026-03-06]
CAD/Final Setup/Curved Environment.SLDPRT
209.0 x 50.0 x 80.0 mm

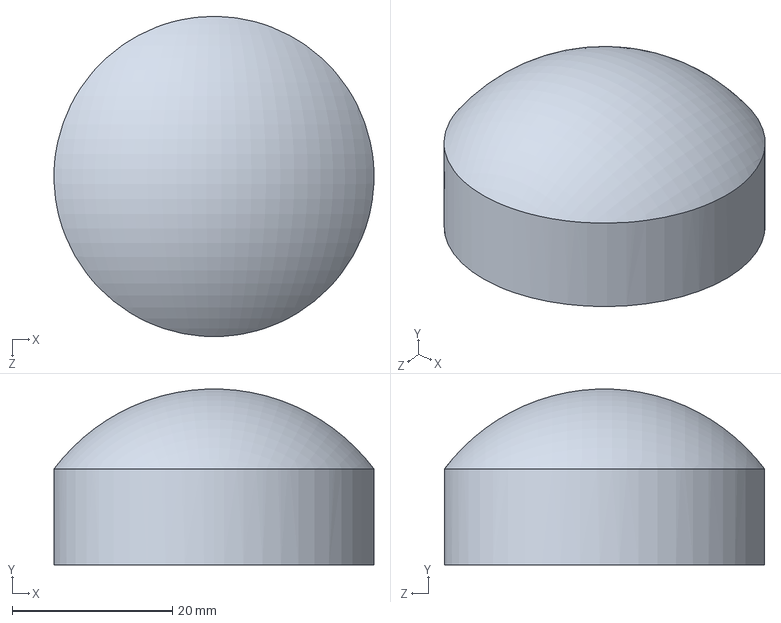
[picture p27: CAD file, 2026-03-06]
CAD/Final Setup/Environment Obstacle.SLDPRT
40.0 x 22.0 x 40.0 mm

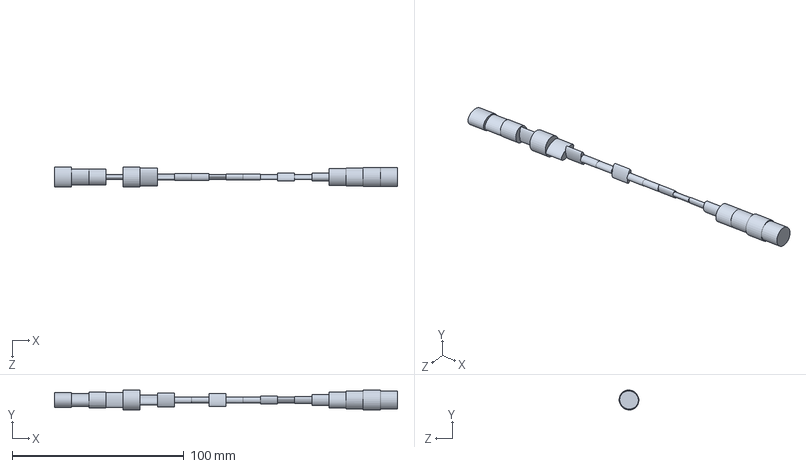
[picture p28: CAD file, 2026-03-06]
CAD/Final Setup/Optimal Beam.SLDPRT
200.0 x 11.6 x 11.7 mm

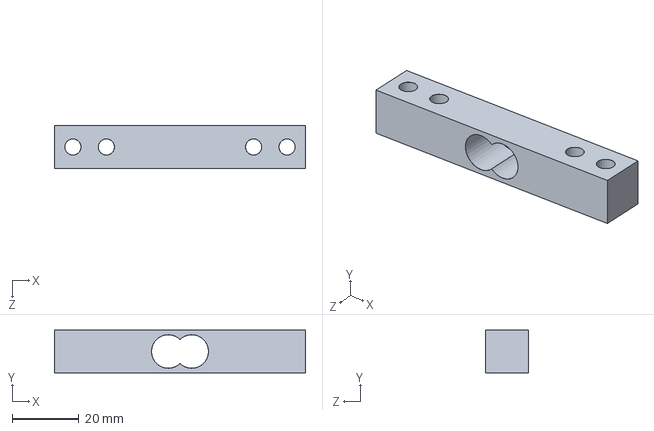
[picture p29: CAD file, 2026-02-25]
CAD/Final Setup/Load Cell.SLDPRT
75.0 x 12.7 x 12.7 mm

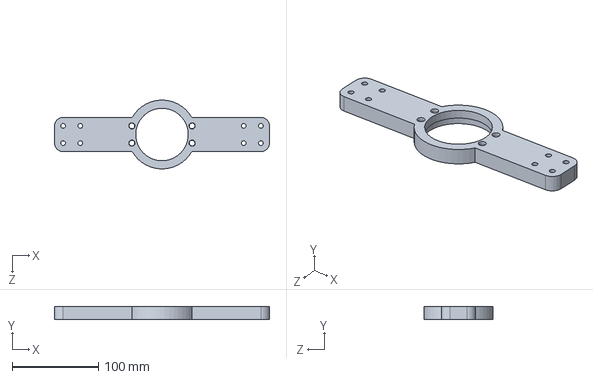
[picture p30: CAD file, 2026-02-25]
CAD/Final Setup/Horizontal Spin.SLDPRT
250.0 x 15.0 x 79.8 mm

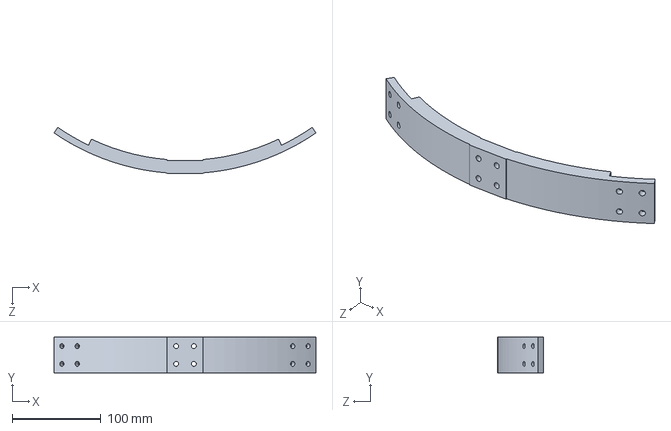
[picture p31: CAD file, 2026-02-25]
CAD/Final Setup/Outer Hat.SLDPRT
294.9 x 40.0 x 52.0 mm

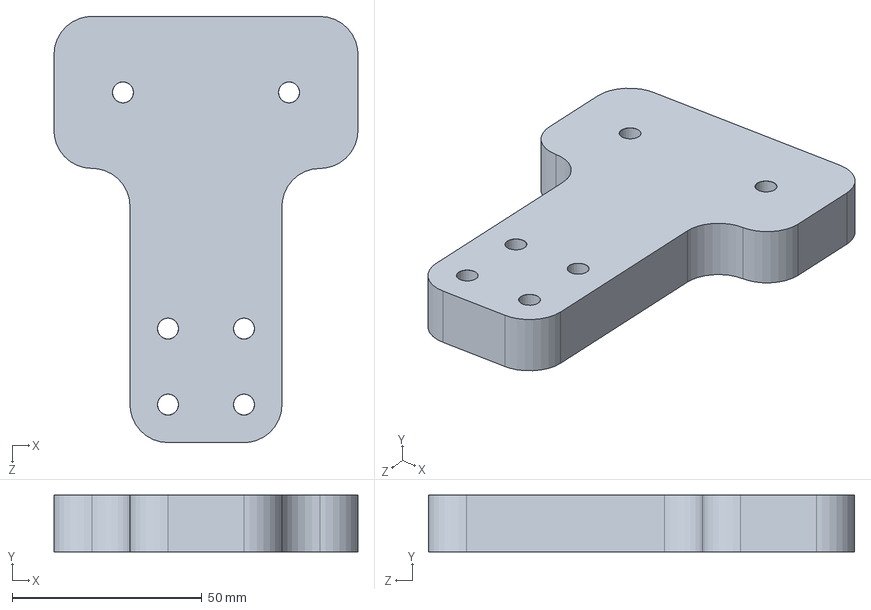
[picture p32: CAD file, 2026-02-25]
CAD/Final Setup/Top Part Inner.SLDPRT
80.0 x 15.0 x 112.2 mm

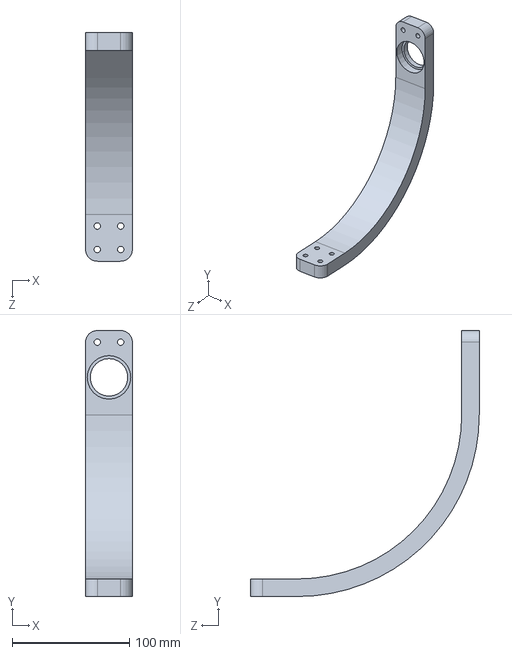
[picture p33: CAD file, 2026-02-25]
CAD/Final Setup/Outer Elbow Bottom.SLDPRT
40.0 x 227.0 x 195.0 mm

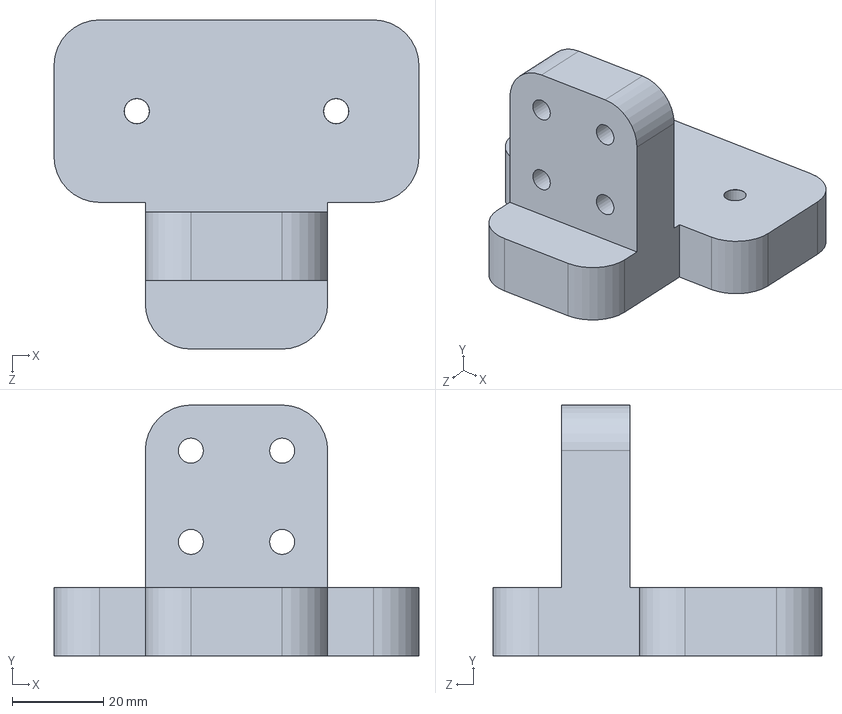
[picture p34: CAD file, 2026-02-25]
CAD/Final Setup/Top Part Outer.SLDPRT
80.0 x 55.0 x 72.2 mm

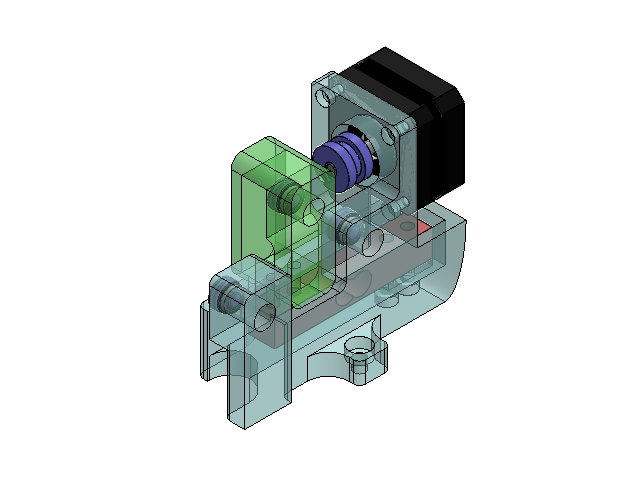
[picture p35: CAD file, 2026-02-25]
CAD/Final Setup/Pully Assembly (Big Motor).SLDASM
Pully Frame
Load Cell
Flexure Mechanism
57155K472_Flanged Ball Bearing x 3
Small Pully x 3
back_plate
front_plate
stator
625ZZ x 2
rotor
connector
M3_screw x 4
Big Pully

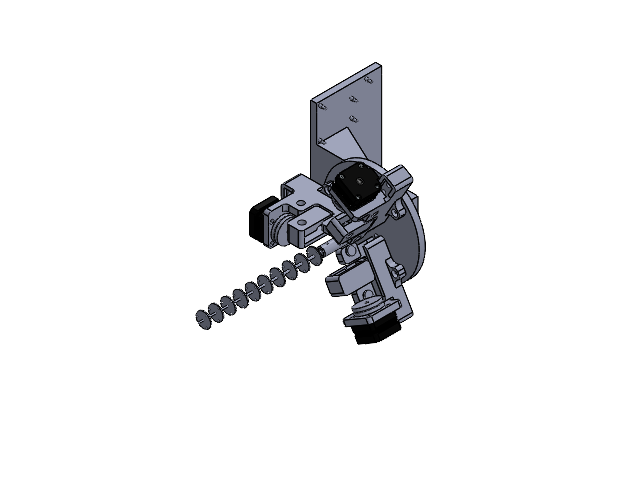
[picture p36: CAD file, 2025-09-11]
CAD/Final Setup/Final Assembly.SLDASM
FT Sensor Mounting Plate
ATI-9105-TW-Mini40-R-X_X-IP65
Sensor_Beam_Adapter
Pully Frame x 3
Load Cell x 3
Flexure Mechanism x 3
Big Pully x 3
57155K472_Flanged Ball Bearing x 9
Small Pully x 9
back_plate x 3
front_plate x 3
stator x 3
625ZZ x 6
rotor x 3
connector x 3
M3_screw x 12
Final Beam

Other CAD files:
CAD/Final Setup/Nema 17 Motor/nema17_pancake.SLDASM
CAD/Final Setup/Nema 17 Motor/625ZZ.SLDPRT
CAD/Final Setup/Nema 17 Motor/back_plate.SLDPRT
CAD/Final Setup/Nema 17 Motor/stator.SLDPRT
CAD/Final Setup/Nema 17 Motor/connector.SLDPRT
CAD/Final Setup/Nema 17 Motor/rotor.SLDPRT
CAD/Final Setup/Nema 17 Motor/front_plate.SLDPRT
CAD/Final Setup/57155K472_Flanged Ball Bearing.SLDPRT
CAD/Final Setup/5972K245_Ball Bearing.SLDPRT
CAD/Final Setup/6656K142_Ultra-Thin Ball Bearing.SLDPRT
CAD/Final Setup/ATI-9105-TW-Mini40-R-X_X-IP65.SLDPRT
CAD/Final Setup/Big Pully.SLDPRT
CAD/Final Setup/Double Tapered Beam.SLDPRT
CAD/Final Setup/Electronics Box.SLDPRT
CAD/Final Setup/Elliptical Beam.SLDPRT
CAD/Final Setup/Flexure Mechanism.SLDPRT
CAD/Final Setup/Friction Hinge.SLDPRT
CAD/Final Setup/Horizontal Small.SLDPRT
CAD/Final Setup/Horizontal Spin Top.SLDPRT
CAD/Final Setup/Inner Elbow Bottom.SLDPRT
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

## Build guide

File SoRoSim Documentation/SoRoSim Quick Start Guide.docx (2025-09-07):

SoRoSim Toolbox V7.0 – MATLAB Installation Guide

# 1. Downloading SoRoSim Toolbox

1. Go to: https://www.mathworks.com/matlabcentral/fileexchange/83038-sorosim and download the V7.0 .zip file from the Version History tab.

2. Unzip the file and place the folder in a convenient location (recommended: Documents\MATLAB).

3. Open MATLAB and add the toolbox to your path by typing in the Command Window:

addpath(genpath('SoRoSim folder location'))

4. Verify installation by typing path. You should see the SoRoSim folder, and its subfolders listed.

# 2. Installing Optimization Toolbox (skip if already installed)

1. In MATLAB, go to HOME → Add-Ons → Get Add-Ons.

2. Search for Optimization Toolbox and install it.

# 3. Creating a SoRoSim Link

1. Create a link with:

L1 = SorosimLink

2. Select:

- Soft → deformable links
- Rigid → non-deformable links

3. For Soft Links, define the following properties:

- Joint type – degrees of freedom at the proximal end
- Cross section – link geometry
- Joint stiffness – (set to 0 for rigid joint)
- Divisions – number of cross-section variations (default = 1)
- Density – e.g., PLA = 1240 kg/m³
- Young’s Modulus (E) – PLA ≈ 2.4×10⁹ Pa
- Poisson’s Ratio (ν) – PLA ≈ 0.34
- Material damping – for dynamics (0 for statics)
- Length
- Initial radius
- Final radius

## Soft Link Material Defaults (PLA)

Property | Symbol | Typical Value | Units | Notes
Density | ρ | 1240 | kg/m³ | Use 0 for statics where mass is ignored
Young's Modulus | E | 2.4×10⁹ | Pa | Material stiffness
Poisson’s Ratio | ν | 0.34 | — | Transverse contraction
Material Damping | c | 0 (statics) | — | Only for dynamic simulations

Geometry fields (Length, Initial radius, Final radius) depend on your design. leave Divisions = 1 unless you need varying cross-sections or varying tendon actuation on specific sections of the length.

# 4. Creating a SoRoSim Linkage

1. Create a linkage with:

S1 = SorosimLinkage(L1)

2. Select the link name and define the proximal-end location/orientation. Click Apply for preview, Done to confirm.

3. Define linkage DOFs (recommended order = 3 for nonlinear bending).

4. Set quadrature points (20+ recommended). All links must use the same number to avoid errors.

5. Specify closed-loop joints (usually 0).

6. Enable/disable gravity and set its direction.

7. Add point forces if desired:

- Choose local frame (follower wrench) or global frame (non-follower wrench)
- Select link, division (usually 1), and position (0 = proximal, 1 = distal)
- Define wrench vector

8. Define if the system is actuated:

- Proximal joint: Choose wrench control (input wrench → solve for position) or position control (input position → solve for wrench)
- Soft actuators (tendons): Define number, path type, and link divisions. Useful for antagonistic wrists. During simulation, input tendon tensions.

# 5. Saving and Loading Models

Save a model:

cd('chosen_directory')
save('model_name.mat','link_variable_name','linkage_variable_name')

Load a model:

cd('directory_of_saved_model')
load('model_name.mat')

Your link and linkage variables will reappear in the Workspace.

# 6. Running a Statics Simulation

1. For a linkage called S1, run a statics simulation with:

S1.statics()

2. You will be prompted to enter joint values: initial position for position-controlled joints, and initial wrench for wrench-controlled joints.

3. If you have tendons, you will be prompted to enter the tension in each tendon.

4. You will be prompted to enter an initial guess for joint/coordinate wrenches. Leave this as all zeros.

5. The solver computes the deflected configuration and outputs the final shape along with the resulting wrench or position of each joint in the deflected state.

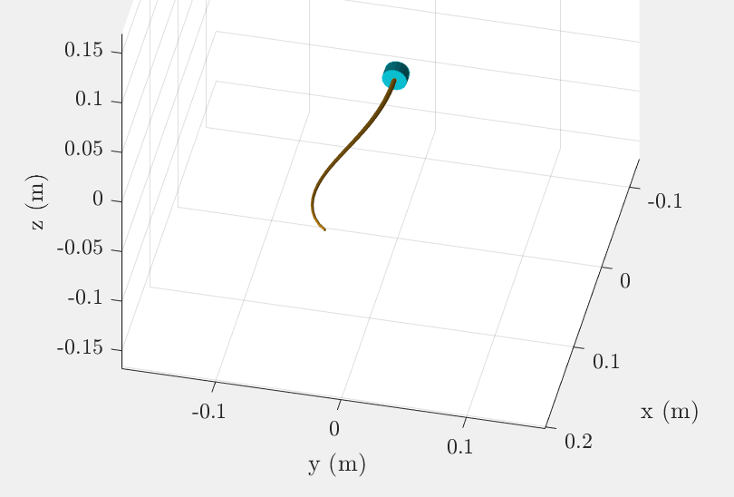
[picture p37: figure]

Figure 1: A statics simulation of a tapered beam with a point force acting in the -y direction and tendon actuation curving the continuum robot to the right.

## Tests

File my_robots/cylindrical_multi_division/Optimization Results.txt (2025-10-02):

r = {4.81, 6.00, 6.00, 6.00, 3.04, 1.88, 2.63, 2.80, 2.78, 1.48, 3.09, 1.39, 1.25, 1.27, 1.25, 1.25, 1.46, 2.49, 3.65, 3.50}
fval = -0.0629
100 samples
0.05 min distance for s

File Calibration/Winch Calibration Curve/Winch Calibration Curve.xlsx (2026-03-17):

 |  |  |  |  | Winch 2
 |  |  |  |  | Measured Load Cell Force (N)
Screw + Nut Weight (g) | Screw + Nut Weight (N) | Weight (g) | Force (N) | Total Force Applied | Trial 1 | Trial 2 | Trial 3
4.86 | 0.0477 | 20 | 0.1962 | 0.2439 | 0.27 | 0.28 | 0.27
 |  | 40 | 0.3924 | 0.4401 | 0.46 | 0.37 | 0.47
 |  | 60 | 0.5886 | 0.6363 | 0.63 | 0.65 | 0.62
 |  | 80 | 0.7848 | 0.8325 | 0.86 | 0.77 | 0.79
 |  | 100 | 0.9810 | 1.0287 | 0.98 | 1.01 | 0.95
 |  | 110 | 1.0791 | 1.1268 | 1.08 | 1.07 | 1.09
 |  | 130 | 1.2753 | 1.3230 | 1.27 | 1.26 | 1.30
 |  | 150 | 1.4715 | 1.5192 | 1.47 | 1.44 | 1.43
 | Chart Data
 | Total Force Applied (N) | Mean Measured Force (N) | Std Dev | Ideal (1:1) | Regression Fit | MAE Label X | MAE Label Y
 | 0.2439 | 0.2733 | 0.0058 | 0.2439 | 0.2629 | 1.25 | 0.4
 | 0.4401 | 0.4333 | 0.0551 | 0.4401 | 0.4450
 | 0.6363 | 0.6333 | 0.0153 | 0.6363 | 0.6272
 | 0.8325 | 0.8067 | 0.0473 | 0.8325 | 0.8093
 | 1.0287 | 0.9800 | 0.0300 | 1.0287 | 0.9915
 | 1.1268 | 1.0800 | 0.0100 | 1.1268 | 1.0825
 | 1.3230 | 1.2767 | 0.0208 | 1.3230 | 1.2647
 | 1.5192 | 1.4467 | 0.0208 | 1.5192 | 1.4468
 | Key Calibration Statistics
 | Linear Regression
 | Slope | 0.928363
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

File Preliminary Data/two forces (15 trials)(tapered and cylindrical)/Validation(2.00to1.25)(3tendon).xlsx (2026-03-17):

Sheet: Proximal Validation (double)
Ground Truth |  |  |  |  |  |  |  |  |  |  | 6-Axis FT Sensor |  |  |  |  |  | SoRoSim get_proximal_value |  |  |  |  |  | Proximal Errors
F1 (N) | s1 (m) | el1 (rad) | az1 (rad) | F2 (N) | s2 (m) | el2 (rad) | az2 (rad) | tau1 (N) | tau2 (N) | tau3 (N) | Tx (Nm) | Ty (Nm) | Tz(Nm) | Fx (N) | Fy (N) | Fz (N) | Tx (Nm) | Ty (Nm) | Tz(Nm) | Fx (N) | Fy (N) | Fz (N) | Tx (Nm) | Ty (Nm) | Tz(Nm) | Fx (N) | Fy (N) | Fz (N)
0.300 | 0.200 | 1.570 | 1.571 | 0.300 | 0.080 | 3.142 | 1.571 | 0.000 | 0.000 | 0.000 | -0.0004305930343 | -0.042 | -0.054 | -0.011 | -0.322 | 0.112 | 1.028193911e-10 | -0.084 | -0.051 | -0.111 | -0.297 | 0.282 | -0.0004305931371 | 0.042 | -0.004 | 0.100 | -0.026 | -0.170
0.400 | 0.100 | 1.570 | 1.571 | 0.500 | 0.060 | 4.712 | 1.571 | 0.800 | 0.000 | 0.000 | -0.001 | -0.019 | 0.001 | -0.003 | 0.007 | -0.031 | 0.0002714307931 | -0.001 | 1.749756135e-05 | -0.006 | -3.56044849e-05 | -0.100 | -0.001 | -0.018 | 0.001 | 0.003 | 0.008 | 0.070
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

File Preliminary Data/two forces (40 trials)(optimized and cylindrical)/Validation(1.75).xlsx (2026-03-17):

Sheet: Proximal Validation (double)
Ground Truth |  |  |  |  |  |  |  |  |  |  | 6-Axis FT Sensor |  |  |  |  |  | SoRoSim get_proximal_value |  |  |  |  |  | Proximal Errors
F1 (N) | s1 (m) | el1 (rad) | az1 (rad) | F2 (N) | s2 (m) | el2 (rad) | az2 (rad) | tau1 (N) | tau2 (N) | tau3 (N) | Tx (Nm) | Ty (Nm) | Tz(Nm) | Fx (N) | Fy (N) | Fz (N) | Tx (Nm) | Ty (Nm) | Tz(Nm) | Fx (N) | Fy (N) | Fz (N) | Tx (Nm) | Ty (Nm) | Tz(Nm) | Fx (N) | Fy (N) | Fz (N)
0.200 | 0.100 | 1.571 | 1.571 | 1.000 | 0.040 | 3.142 | 1.571 | 1.400 | 0.000 | 0.000 | -8.469540626e-05 | -0.011 | -0.130 | 0.019 | -0.972 | 0.029 | 0.001 | -0.038 | -0.130 | -0.034 | -1.000 | 0.199 | -0.001 | 0.026 | -0.001 | 0.052 | 0.028 | -0.170
1.000 | 0.100 | 1.571 | 1.571 | 1.000 | 0.080 | 3.142 | 1.571 | 0.000 | 0.000 | 0.000 | -0.001 | -0.187 | -0.149 | -0.459 | -0.810 | 0.925 | 0.000 | -0.185 | -0.167 | -0.376 | -0.970 | 0.958 | -0.001 | -0.002 | 0.018 | -0.082 | 0.160 | -0.033
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

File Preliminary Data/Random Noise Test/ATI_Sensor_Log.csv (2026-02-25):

1/14/2026 11:33:45 AM | 0.000158787224791013 | -6.3083520217333E-05 | 0.000562187866307795 | 6.28982297712355E-06 | 3.47054128724267E-06 | -3.4584634249768E-06
1/14/2026 11:35:07 AM | -0.00092765869339928 | -1.33946887217462E-05 | -0.000981004443019629 | 2.88837986772705E-06 | -1.88465310202446E-05 | -1.60878016686183E-06
1/14/2026 11:35:49 AM | 0.397724568843842 | -0.00150185637176037 | -0.267172366380692 | -0.00229362677782774 | 0.129284635186195 | -0.000309971743263304
1/14/2026 11:36:53 AM | 0.801318764686584 | -0.00261756405234337 | -0.551415801048279 | -0.00510405329987407 | 0.265066742897034 | -0.00131723959930241
1/14/2026 11:37:40 AM | 0.964142620563507 | -0.00328068062663078 | -0.674024820327759 | -0.00623468263074756 | 0.318444460630417 | -0.0017683464102447
1/14/2026 11:38:35 AM | 0.810019016265869 | -0.00186469033360481 | -0.558775246143341 | -0.00528598437085748 | 0.266178816556931 | -0.00156343937851489
1/14/2026 11:39:16 AM | 0.412475854158401 | 0.000946316868066788 | -0.272229909896851 | -0.00249370909295976 | 0.12970544397831 | -0.00060571008361876
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

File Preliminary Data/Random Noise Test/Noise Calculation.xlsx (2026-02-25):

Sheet: Proximal Validation (double)
Ground Truth |  |  |  |  |  |  |  |  |  |  | 6-Axis FT Sensor |  |  |  |  |  | SoRoSim get_proximal_value |  |  |  |  |  | Proximal Errors
F1 (N) | s1 (m) | el1 (rad) | az1 (rad) | F2 (N) | s2 (m) | el2 (rad) | az2 (rad) | tau1 (N) | tau2 (N) | tau3 (N) | Tx (Nm) | Ty (Nm) | Tz(Nm) | Fx (N) | Fy (N) | Fz (N) | Tx (Nm) | Ty (Nm) | Tz(Nm) | Fx (N) | Fy (N) | Fz (N) | Tx (Nm) | Ty (Nm) | Tz(Nm) | Fx (N) | Fy (N) | Fz (N)
0.300 | 0.200 | 1.570 | 1.571 | 0.300 | 0.080 | 3.142 | 1.571 | 0.000 | 0.000 | 0.000 |  |  |  |  |  |  |  |  |  |  |  |  | 0.000 | 0.000 | 0.000 | 0.000 | 0.000 | 0.000
0.400 | 0.100 | 1.570 | 1.571 | 0.500 | 0.060 | 4.712 | 1.571 | 0.800 | 0.000 | 0.000 | -0.001 | -0.007 | -0.0003412742808 | -0.056 | -0.001 | -0.078 | 0.0002856979958 | -0.001 | 2.174307973e-05 | -0.004 | -1.553727893e-05 | -0.100 | -0.001 | -0.006 | -0.0003630173605 | -0.051 | -0.001 | 0.022
0.700 | 0.160 | 1.570 | 1.571 | 0.700 | 0.020 | 4.712 | 1.571 | 0.000 | 0.000 | 0.000 | -0.001 | -0.079 | -0.001 | -0.291 | -0.005 | -0.150 | -5.941468702e-14 | -0.092 | 0.0001041313821 | -0.219 | 0.0002402900112 | -0.056 | -0.001 | 0.013 | -0.001 | -0.072 | -0.005 | -0.094
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

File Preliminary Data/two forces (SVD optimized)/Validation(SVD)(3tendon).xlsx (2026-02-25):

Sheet: Proximal Validation (empirical)
Ground Truth |  |  |  |  |  |  |  |  | 6-Axis FT Sensor |  |  |  |  |  | SoRoSim get_proximal_value |  |  |  |  |  | Proximal Errors
F1 (N) | s1 (m) | theta1 (rad) | F2 (N) | s2 (m) | theta2 (rad) | tau1 (N) | tau2 (N) | tau3 (N) | Tx (Nm) | Ty (Nm) | Tz(Nm) | Fx (N) | Fy (N) | Fz (N) | Tx (Nm) | Ty (Nm) | Tz(Nm) | Fx (N) | Fy (N) | Fz (N) | Tx (Nm) | Ty (Nm) | Tz(Nm) | Fx (N) | Fy (N) | Fz (N) | singular values
0.800 | 0.160 | 3.927 | 0.800 | 0.020 | 3.665 | 0.000 | 0.000 | 0.000 | 0.00697 | 0.18634 | -0.22898 | -0.40629 | -1.22047 | -0.89388 | 0.0014 | 0.1788 | -0.2113 | -0.3160 | -1.2155 | -0.9252 | 0.006 | 0.007 | -0.018 | -0.090 | -0.005 | 0.031 | 2.42
0.800 | 0.200 | 3.927 | 0.400 | 0.040 | 1.047 | 0.000 | 0.000 | 0.000 |  |  |  |  |  |  | -0.0001 | 0.0974 | -0.1215 | -0.4388 | -0.2683 | -0.1057 | 7.854140843e-05 | -0.097 | 0.121 | 0.439 | 0.268 | 0.106 | 2.28
0.600 | 0.200 | 2.618 | 0.800 | 0.020 | 2.356 | 0.000 | 0.000 | 0.000 |  |  |  |  |  |  | 0.0003 | -0.1423 | -0.2036 | -0.2774 | -1.0348 | 0.8310 | -0.0003 | 0.142 | 0.204 | 0.277 | 1.035 | -0.831 | 2.213207
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

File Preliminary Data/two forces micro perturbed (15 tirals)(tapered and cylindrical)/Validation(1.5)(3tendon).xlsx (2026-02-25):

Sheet: Proximal Validation
Ground Truth |  |  |  |  |  |  |  |  |  |  | 6-Axis FT Sensor |  |  |  |  |  | SoRoSim get_proximal_value |  |  |  |  |  | Proximal Errors
F1 (N) | s1 (m) | el1 (rad) | az1 (rad) | F2 (N) | s2 (m) | el2 (rad) | az2 (rad) | tau1 (N) | tau2 (N) | tau3 (N) | Tx (Nm) | Ty (Nm) | Tz(Nm) | Fx (N) | Fy (N) | Fz (N) | Tx (Nm) | Ty (Nm) | Tz(Nm) | Fx (N) | Fy (N) | Fz (N) | Tx (Nm) | Ty (Nm) | Tz(Nm) | Fx (N) | Fy (N) | Fz (N)
0.500 | 0.120 | 1.570 | 1.571 | 0.300 | 0.020 | 3.142 | 1.571 | 0.800 | 0.000 | 0.000 | 0.003 | -0.085 | -0.033 | -0.186 | -0.291 | 0.341 | 0.002 | -0.101 | -0.033 | -0.187 | -0.303 | 0.463 | 0.001 | 0.016 | 0.0002973497138 | 0.001 | 0.012 | -0.122
0.500 | 0.120 | 1.570 | 1.571 | 0.700 | 0.060 | 4.712 | 1.571 | 0.000 | 0.000 | 0.000 | 0.0002920636907 | -0.014 | 0.001 | -0.014 | -0.004 | -0.148 | -1.355913705e-13 | 0.001 | 4.197974784e-05 | -0.017 | 0.0001195215652 | -0.206 | 0.0002920636909 | -0.015 | 0.0004722119439 | 0.003 | -0.004 | 0.058
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

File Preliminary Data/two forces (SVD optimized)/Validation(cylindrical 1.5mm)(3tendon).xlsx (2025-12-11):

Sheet: Proximal Validation (empirical)
Ground Truth |  |  |  |  |  |  |  |  | 6-Axis FT Sensor |  |  |  |  |  | SoRoSim get_proximal_value |  |  |  |  |  | Proximal Errors
F1 (N) | s1 (m) | theta1 (rad) | F2 (N) | s2 (m) | theta2 (rad) | tau1 (N) | tau2 (N) | tau3 (N) | Tx (Nm) | Ty (Nm) | Tz(Nm) | Fx (N) | Fy (N) | Fz (N) | Tx (Nm) | Ty (Nm) | Tz(Nm) | Fx (N) | Fy (N) | Fz (N) | Tx (Nm) | Ty (Nm) | Tz(Nm) | Fx (N) | Fy (N) | Fz (N) | singular values
0.800 | 0.160 | 3.927 | 0.800 | 0.020 | 3.665 | 0.000 | 0.000 | 0.000 | 0.00326 | 0.18071 | -0.20451 | -0.73947 | -1.01043 | -0.82137 | 0.0000 | 0.1530 | -0.1846 | -0.8358 | -0.9899 | -0.7009 | 0.003 | 0.028 | -0.020 | 0.096 | -0.021 | -0.120 | 2.42
0.800 | 0.200 | 3.927 | 0.400 | 0.040 | 1.047 | 0.000 | 0.000 | 0.000 |  |  |  |  |  |  |  |  |  |  |  |  | 0.000 | 0.000 | 0.000 | 0.000 | 0.000 | 0.000 | 2.28
0.600 | 0.200 | 2.618 | 0.800 | 0.020 | 2.356 | 0.000 | 0.000 | 0.000 |  |  |  |  |  |  |  |  |  |  |  |  | 0.000 | 0.000 | 0.000 | 0.000 | 0.000 | 0.000 | 2.213207
0.800 | 0.180 | 2.618 | 0.700 | 0.060 | 2.356 | 0.000 | 0.000 | 0.000 |  |  |  |  |  |  |  |  |  |  |  |  | 0.000 | 0.000 | 0.000 | 0.000 | 0.000 | 0.000 | 1.89
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

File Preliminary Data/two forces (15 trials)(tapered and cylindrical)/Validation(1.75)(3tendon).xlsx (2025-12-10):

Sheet: Proximal Validation (double)
Ground Truth |  |  |  |  |  |  |  |  |  |  | 6-Axis FT Sensor |  |  |  |  |  | SoRoSim get_proximal_value |  |  |  |  |  | Proximal Errors
F1 (N) | s1 (m) | el1 (rad) | az1 (rad) | F2 (N) | s2 (m) | el2 (rad) | az2 (rad) | tau1 (N) | tau2 (N) | tau3 (N) | Tx (Nm) | Ty (Nm) | Tz(Nm) | Fx (N) | Fy (N) | Fz (N) | Tx (Nm) | Ty (Nm) | Tz(Nm) | Fx (N) | Fy (N) | Fz (N) | Tx (Nm) | Ty (Nm) | Tz(Nm) | Fx (N) | Fy (N) | Fz (N)
0.300 | 0.200 | 1.570 | 1.571 | 0.300 | 0.080 | 3.142 | 1.571 | 0.000 | 0.000 | 0.000 |  |  |  |  |  |  |  |  |  |  |  |  | 0.000 | 0.000 | 0.000 | 0.000 | 0.000 | 0.000
0.400 | 0.100 | 1.570 | 1.571 | 0.500 | 0.060 | 4.712 | 1.571 | 0.800 | 0.000 | 0.000 | -0.001 | -0.007 | -0.0003412742808 | -0.056 | -0.001 | -0.078 | 0.0002856979958 | -0.001 | 2.174307973e-05 | -0.004 | -1.553727893e-05 | -0.100 | -0.001 | -0.006 | -0.0003630173605 | -0.051 | -0.001 | 0.022
0.700 | 0.160 | 1.570 | 1.571 | 0.700 | 0.020 | 4.712 | 1.571 | 0.000 | 0.000 | 0.000 | -0.001 | -0.079 | -0.001 | -0.291 | -0.005 | -0.150 | -5.941468702e-14 | -0.092 | 0.0001041313821 | -0.219 | 0.0002402900112 | -0.056 | -0.001 | 0.013 | -0.001 | -0.072 | -0.005 | -0.094
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

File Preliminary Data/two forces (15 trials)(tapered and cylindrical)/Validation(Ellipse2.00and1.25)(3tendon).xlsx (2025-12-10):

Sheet: Proximal Validation (double)
Ground Truth |  |  |  |  |  |  |  |  | 6-Axis FT Sensor |  |  |  |  |  | SoRoSim get_proximal_value |  |  |  |  |  | Proximal Errors
F1 (N) | s1 (m) | el1 (rad) | F2 (N) | s2 (m) | el2 (rad) | tau1 (N) | tau2 (N) | tau3 (N) | Tx (Nm) | Ty (Nm) | Tz(Nm) | Fx (N) | Fy (N) | Fz (N) | Tx (Nm) | Ty (Nm) | Tz(Nm) | Fx (N) | Fy (N) | Fz (N) | Tx (Nm) | Ty (Nm) | Tz(Nm) | Fx (N) | Fy (N) | Fz (N)
0.700 | 0.180 | 2.356 | 0.800 | 0.060 | 3.142 | 0.800 | 0.000 | 0.000 | 0.0323 | -0.0552 | -0.1895 | -0.6798 | -0.9223 | -0.1120 |  |  |  |  |  |  | 0.032 | -0.055 | -0.190 | -0.680 | -0.922 | -0.112
0.600 | 0.120 | 2.356 | 0.300 | 0.040 | 3.927 | 0.400 | 0.000 | 0.000 | 0.0115 | -0.0497 | -0.1265 | -0.3520 | -0.6694 | 0.0731 |  |  |  |  |  |  | 0.012 | -0.050 | -0.127 | -0.352 | -0.669 | 0.073
0.800 | 0.120 | 2.356 | 0.500 | 0.060 | 3.927 | 0.400 | 0.000 | 0.000 | 0.0122 | -0.0559 | -0.1396 | -0.4911 | -0.6653 | 0.0492 |  |  |  |  |  |  | 0.012 | -0.056 | -0.140 | -0.491 | -0.665 | 0.049
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

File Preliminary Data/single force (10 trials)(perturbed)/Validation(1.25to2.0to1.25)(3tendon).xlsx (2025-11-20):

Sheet: Proximal Validation
Ground Truth |  |  |  |  |  | 6-Axis FT Sensor |  |  |  |  |  | SoRoSim get_proximal_value |  |  |  |  |  | Proximal Errors
F (N) | s (m) | theta (rad) | tau1 (N) | tau2 (N) | tau3 (N) | Tx (Nm) | Ty (Nm) | Tz(Nm) | Fx (N) | Fy (N) | Fz (N) | Tx (Nm) | Ty (Nm) | Tz(Nm) | Fx (N) | Fy (N) | Fz (N) | Tx (Nm) | Ty (Nm) | Tz(Nm) | Fx (N) | Fy (N) | Fz (N)
0.400 | 0.060 | 1.571 | 0.000 | 0.000 | 0.000 | 0.0004286323674 | -0.060 | -0.000255721563 | -0.041 | 0.001 | 0.381 |  |  |  |  |  |  | 0.0004286323674 | -0.060 | -0.000255721563 | -0.041 | 0.001 | 0.381
0.800 | 0.060 | 1.571 | 0.000 | 0.000 | 0.000 | 0.001 | -0.133 | -0.0002361295046 | -0.198 | 0.004 | 0.836 |  |  |  |  |  |  | 0.001 | -0.133 | -0.0002361295046 | -0.198 | 0.004 | 0.836
0.300 | 0.080 | 1.571 | 0.000 | 0.000 | 0.000 | 0.0001679906854 | -0.046 | -0.0003884102625 | -0.034 | -0.001 | 0.254 |  |  |  |  |  |  | 0.0001679906854 | -0.046 | -0.0003884102625 | -0.034 | -0.001 | 0.254
0.500 | 0.100 | 1.571 | 0.000 | 0.000 | 0.000 | 0.0003343684366 | -0.092 | -0.001 | -0.137 | -0.003 | 0.447 |  |  |  |  |  |  | 0.0003343684366 | -0.092 | -0.001 | -0.137 | -0.003 | 0.447
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

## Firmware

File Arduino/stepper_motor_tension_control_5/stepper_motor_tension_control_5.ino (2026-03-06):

/*
  Stepper Motor Tension Control System
  Controls 5 motors to reach user-specified string tensions
*/

#include <TMCStepper.h>
#include <HX711_ADC.h>

// Motor pin connections
const int MOTOR1_STEP_PIN = 31, MOTOR1_DIR_PIN = 32, MOTOR1_EN_PIN = 30;
const int MOTOR2_STEP_PIN = 34, MOTOR2_DIR_PIN = 35, MOTOR2_EN_PIN = 33;
const int MOTOR3_STEP_PIN = 37, MOTOR3_DIR_PIN = 38, MOTOR3_EN_PIN = 36;
const int MOTOR4_STEP_PIN = 40, MOTOR4_DIR_PIN = 41, MOTOR4_EN_PIN = 39;
const int MOTOR5_STEP_PIN = 43, MOTOR5_DIR_PIN = 44, MOTOR5_EN_PIN = 42;

// Load cell pin connections
const int LOADCELL1_DOUT_PIN = 2, LOADCELL1_SCK_PIN = 3;
const int LOADCELL2_DOUT_PIN = 4, LOADCELL2_SCK_PIN = 5;
const int LOADCELL3_DOUT_PIN = 6, LOADCELL3_SCK_PIN = 7;
const int LOADCELL4_DOUT_PIN = 8, LOADCELL4_SCK_PIN = 9;
const int LOADCELL5_DOUT_PIN = 10, LOADCELL5_SCK_PIN = 11;

// Driver settings
const float SENSE_RESISTOR = 0.11;
TMC2209Stepper driver1(&Serial1, SENSE_RESISTOR, 0);
TMC2209Stepper driver2(&Serial1, SENSE_RESISTOR, 1);
TMC2209Stepper driver3(&Serial1, SENSE_RESISTOR, 2);
TMC2209Stepper driver4(&Serial1, SENSE_RESISTOR, 3);
TMC2209Stepper driver5(&Serial2, SENSE_RESISTOR, 0);

// Load cell objects
HX711_ADC LoadCell1(LOADCELL1_DOUT_PIN, LOADCELL1_SCK_PIN);
HX711_ADC LoadCell2(LOADCELL2_DOUT_PIN, LOADCELL2_SCK_PIN);
HX711_ADC LoadCell3(LOADCELL3_DOUT_PIN, LOADCELL3_SCK_PIN);
HX711_ADC LoadCell4(LOADCELL4_DOUT_PIN, LOADCELL4_SCK_PIN);
HX711_ADC LoadCell5(LOADCELL5_DOUT_PIN, LOADCELL5_SCK_PIN);

// Load cell calibration factor
const float CALIBRATION_FACTOR = 130000.0;

// Control variables
float targetTension1 = 0, targetTension2 = 0, targetTension3 = 0, targetTension4 = 0, targetTension5 = 0;
const float TOLERANCE = 0.03;       // Stop when within this range of target
const float TENDON_TOLERANCE = 0.08;  // NEW
const float ZERO_TOLERANCE = 0.05;  // Stop when within this range of home
bool returningToZero = false;       // Flag to track when returning to zero after cancel

// NEW: Per-motor timing for delay-based speed control
unsigned long lastStepTime[5] = {0, 0, 0, 0, 0};

void setup() {
  Serial.begin(115200);
  Serial.println("Tension Control System Starting...");
  
  setupMotors();
  setupLoadCells();
  getUserTargets();
  
  Serial.println("System ready. Motors will adjust to target tensions.");
  Serial.println("Send 'c' anytime to cancel and set tensions to zero.");
}

void loop() {
  // Check for cancel command
  if (Serial.available() > 0) {
    char command = Serial.read();
    if (command == 'c' || command == 'C') {
      targetTension1 = 0;
      targetTension2 = 0;
      targetTension3 = 0;
      targetTension4 = 0;
      targetTension5 = 0;
      returningToZero = true;
      Serial.println("\nOperation cancelled. Target tensions set to zero.");
      while (Serial.available() > 0) {
        Serial.read();
      }
    }
  }
  
  // Read current tensions
  LoadCell1.update();
  LoadCell2.update();
  LoadCell3.update();
  LoadCell4.update();
  LoadCell5.update();
  float tension1 = LoadCell1.getData();
  float tension2 = LoadCell2.getData();
  float tension3 = LoadCell3.getData();
  float tension4 = LoadCell4.getData();
  float tension5 = LoadCell5.getData();
  
  // Check if we've reached zero after cancel and should get new targets
  if (returningToZero && 
      abs(tension1) <= ZERO_TOLERANCE && abs(tension2) <= ZERO_TOLERANCE &&
      abs(tension3) <= ZERO_TOLERANCE && abs(tension4) <= ZERO_TOLERANCE &&
      abs(tension5) <= ZERO_TOLERANCE) {
    Serial.println("Tensions returned to zero. Ready for new targets.");
    returningToZero = false;
    getUserTargets();
    return;
  }
  
  // NEW: Delay-based tension control — 1 step per motor per interval
  int stepPins[] = {MOTOR1_STEP_PIN, MOTOR2_STEP_PIN, MOTOR3_STEP_PIN, MOTOR4_STEP_PIN, MOTOR5_STEP_PIN};
  int dirPins[]  = {MOTOR1_DIR_PIN, MOTOR2_DIR_PIN, MOTOR3_DIR_PIN, MOTOR4_DIR_PIN, MOTOR5_DIR_PIN};
  float errors[] = {tension1 - targetTension1, tension2 - targetTension2, tension3 - targetTension3,
                    tension4 - targetTension4, tension5 - targetTension5};

  unsigned long now = micros();
  for (int i = 0; i < 5; i++) {
      unsigned long interval = (i < 3) ? delayForErrorTendon(errors[i]) : delayForErrorForce(errors[i]);
      float tol = (i < 3) ? TENDON_TOLERANCE : TOLERANCE;
      if (abs(errors[i]) > tol && (now - lastStepTime[i]) >= interval) {
        stepMotor1(stepPins[i], dirPins[i], errors[i] < 0);
        lastStepTime[i] = now;
      }
    }
  
  // Print status for plotting (10Hz update rate)
  static unsigned long lastPrint = 0;
  if (millis() - lastPrint > 100) {
    Serial.print("Tendon Tensions[N]: ");
    Serial.print(tension1, 2); Serial.print(", ");
    Serial.print(tension2, 2); Serial.print(", ");
    Serial.print(tension3, 2);

    Serial.print(" | Forces[N]: ");
    Serial.print(tension4, 2); Serial.print(", ");
    Serial.print(tension5, 2);

    Serial.print(" | Targets: ");
    Serial.print(targetTension1, 2); Serial.print(", ");
    Serial.print(targetTension2, 2); Serial.print(", ");
    Serial.print(targetTension3, 2); Serial.print(", ");
    Serial.print(targetTension4, 2); Serial.print(", ");
    Serial.println(targetTension5, 2);
    lastPrint = millis();
  }

}

// ---- Motor Control ----

void setupMotors() {
  pinMode(MOTOR1_STEP_PIN, OUTPUT); pinMode(MOTOR1_DIR_PIN, OUTPUT); pinMode(MOTOR1_EN_PIN, OUTPUT);
  pinMode(MOTOR2_STEP_PIN, OUTPUT); pinMode(MOTOR2_DIR_PIN, OUTPUT); pinMode(MOTOR2_EN_PIN, OUTPUT);
  pinMode(MOTOR3_STEP_PIN, OUTPUT); pinMode(MOTOR3_DIR_PIN, OUTPUT); pinMode(MOTOR3_EN_PIN, OUTPUT);
  pinMode(MOTOR4_STEP_PIN, OUTPUT); pinMode(MOTOR4_DIR_PIN, OUTPUT); pinMode(MOTOR4_EN_PIN, OUTPUT);
  pinMode(MOTOR5_STEP_PIN, OUTPUT); pinMode(MOTOR5_DIR_PIN, OUTPUT); pinMode(MOTOR5_EN_PIN, OUTPUT);
  digitalWrite(MOTOR1_EN_PIN, HIGH);
  digitalWrite(MOTOR2_EN_PIN, HIGH);
  digitalWrite(MOTOR3_EN_PIN, HIGH);
  digitalWrite(MOTOR4_EN_PIN, HIGH);
  digitalWrite(MOTOR5_EN_PIN, HIGH);
  
  Serial1.begin(115200);
  Serial2.begin(115200);
  delay(10);
  
  initDriver(driver1);
  initDriver(driver2);
  initDriver(driver3);
  initDriver(driver4);
  initDriver(driver5);

  // Fixed 256 microsteps for fine tendon control
  driver1.microsteps(256);
  driver2.microsteps(256);
  driver3.microsteps(256);
  // Fixed 128 microsteps for force application
  driver4.microsteps(128);
  driver5.microsteps(128);

  delay(1000);
  digitalWrite(MOTOR1_EN_PIN, LOW);
  digitalWrite(MOTOR2_EN_PIN, LOW);
  digitalWrite(MOTOR3_EN_PIN, LOW);
  digitalWrite(MOTOR4_EN_PIN, LOW);
  digitalWrite(MOTOR5_EN_PIN, LOW);
  
  Serial.println("Motors configured");
}

void initDriver(TMC2209Stepper &drv) {
  drv.begin();
  drv.toff(5);
  drv.I_scale_analog(false);
  drv.rms_current(1000);
  drv.en_spreadCycle(false);
  drv.pwm_autoscale(true);
  drv.pwm_autograd(true);
}

// Motors 4 & 5 — faster response
unsigned long delayForErrorForce(float error) {
  float absErr = abs(error);
  if (absErr > 0.75) return 10;
  if (absErr > 0.5)  return 400;
  if (absErr > 0.3)  return 2500;
  if (absErr > 0.2)  return 5000;
  if (absErr > 0.1)  return 10000;
  return 20000;
}

// Motors 1, 2 & 3 — slower, finer control
unsigned long delayForErrorTendon(float error) {
  float absErr = abs(error);
  if (absErr > 2.0)  return 200;
  if (absErr > 1.5)  return 400;
  if (absErr > 0.75) return 4000;
  if (absErr > 0.55) return 10000;
  if (absErr > 0.3)  return 15000;
  if (absErr > 0.1)  return 20000;
  return 40000;
}

// NEW: Single-step pulse (no loop, no blocking delay)
void stepMotor1(int stepPin, int dirPin, bool forward) {
  digitalWrite(dirPin, forward ? LOW : HIGH);
  digitalWrite(stepPin, HIGH);
  delayMicroseconds(2);
  digitalWrite(stepPin, LOW);
}

// ---- Load Cells ----

void setupLoadCells() {
  LoadCell1.begin();
  LoadCell2.begin();
  LoadCell3.begin();
  LoadCell4.begin();
  LoadCell5.begin();
  
  unsigned long stabilizingtime = 2000;
  LoadCell1.start(stabilizingtime, true);
  LoadCell2.start(stabilizingtime, true);
  LoadCell3.start(stabilizingtime, true);
  LoadCell4.start(stabilizingtime, true);
  LoadCell5.start(stabilizingtime, true);
  
  LoadCell1.setCalFactor(CALIBRATION_FACTOR);
  LoadCell2.setCalFactor(CALIBRATION_FACTOR);
  LoadCell3.setCalFactor(CALIBRATION_FACTOR);
  LoadCell4.setCalFactor(CALIBRATION_FACTOR);
  LoadCell5.setCalFactor(CALIBRATION_FACTOR);
  
  while (!LoadCell1.update() || !LoadCell2.update() || !LoadCell3.update() || !LoadCell4.update() || !LoadCell5.update());
  
  Serial.println("Load cells calibrated and ready");
}

// ---- User Input ----

void getUserTargets() {
  while (Serial.available() > 0) {
    Serial.read();
  }
  Serial.println("\n--- Set Targets ---");

  Serial.print("Enter target tension for tendon 1 (N): ");
  while (!Serial.available()) {}
  targetTension1 = Serial.parseFloat();
  while (Serial.available() > 0) { Serial.read(); }
  Serial.println(targetTension1, 2);

  Serial.print("Enter target tension for tendon 2 (N): ");
  while (!Serial.available()) {}
  targetTension2 = Serial.parseFloat();
  while (Serial.available() > 0) { Serial.read(); }
  Serial.println(targetTension2, 2);

  Serial.print("Enter target tension for tendon 3 (N): ");
  while (!Serial.available()) {}
  targetTension3 = Serial.parseFloat();
  while (Serial.available() > 0) { Serial.read(); }
  Serial.println(targetTension3, 2);

  Serial.print("Enter target for Force 1 (N): ");
  while (!Serial.available()) {}
  targetTension4 = Serial.parseFloat();
  while (Serial.available() > 0) { Serial.read(); }
  Serial.println(targetTension4, 2);

  Serial.print("Enter target for Force 2 (N): ");
  while (!Serial.available()) {}
  targetTension5 = Serial.parseFloat();
  while (Serial.available() > 0) { Serial.read(); }
  Serial.println(targetTension5, 2);

  Serial.println("Targets set. Starting tension control...\n");
}

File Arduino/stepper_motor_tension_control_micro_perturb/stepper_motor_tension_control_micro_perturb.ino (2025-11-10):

/*
  Stepper Motor Tension Control System
  Controls 4 motors to reach user-specified string tensions
*/

#include <TMCStepper.h>
#include <HX711_ADC.h>

// Motor pin connections
const int MOTOR1_STEP_PIN = 31, MOTOR1_DIR_PIN = 32, MOTOR1_EN_PIN = 30;
const int MOTOR2_STEP_PIN = 34, MOTOR2_DIR_PIN = 35, MOTOR2_EN_PIN = 33;
const int MOTOR3_STEP_PIN = 37, MOTOR3_DIR_PIN = 38, MOTOR3_EN_PIN = 36;
const int MOTOR4_STEP_PIN = 40, MOTOR4_DIR_PIN = 41, MOTOR4_EN_PIN = 39;

// Load cell pin connections
const int LOADCELL1_DOUT_PIN = 2, LOADCELL1_SCK_PIN = 3;
const int LOADCELL2_DOUT_PIN = 4, LOADCELL2_SCK_PIN = 5;
const int LOADCELL3_DOUT_PIN = 6, LOADCELL3_SCK_PIN = 7;
const int LOADCELL4_DOUT_PIN = 8, LOADCELL4_SCK_PIN = 9;

// Driver settings
const float SENSE_RESISTOR = 0.11;
TMC2209Stepper driver1(&Serial1, SENSE_RESISTOR, 0);
TMC2209Stepper driver2(&Serial1, SENSE_RESISTOR, 1);
TMC2209Stepper driver3(&Serial1, SENSE_RESISTOR, 2);
TMC2209Stepper driver4(&Serial1, SENSE_RESISTOR, 3);

// Load cell objects
HX711_ADC LoadCell1(LOADCELL1_DOUT_PIN, LOADCELL1_SCK_PIN);
HX711_ADC LoadCell2(LOADCELL2_DOUT_PIN, LOADCELL2_SCK_PIN);
HX711_ADC LoadCell3(LOADCELL3_DOUT_PIN, LOADCELL3_SCK_PIN);
HX711_ADC LoadCell4(LOADCELL4_DOUT_PIN, LOADCELL4_SCK_PIN);

// Perturbation array - define your perturbation sizes here
const float perturbations[] = {0.5, 1.0, 1.5};          
const int numPerturbations = sizeof(perturbations) / sizeof(perturbations[0]);

// Control variables
float targetTension1 = 0, targetTension2 = 0, targetTension3 = 0, targetTension4 = 0;
float baseTension1, baseTension2, baseTension3;  // Store original targets
const int STEP_DELAY = 1000;
const float TOLERANCE = 0.03;
const float ZERO_TOLERANCE = 0.05;
bool returningToZero = false;

// Perturbation state variables
bool motor4Frozen = false;
int perturbationIndex = 0;  // Current perturbation (0 to numPerturbations-1)
int motorIndex = 0;  // Current motor (0=motor1, 1=motor2, 2=motor3)

void setup() {
  Serial.begin(115200);
  Serial.println("Tension Control System Starting...");
  
  setupMotors();
  setupLoadCells();
  getUserTargets();
  
  Serial.println("System ready. Motors will adjust to target tensions.");
  Serial.println("Send 's' to start perturbation sequence.");
  Serial.println("Send 'c' anytime to cancel and set tensions to zero.");
}

void loop() {
  // Check for commands
  if (Serial.available() > 0) {
    char command = Serial.read();
    
    // Handle 's' command - perturbation sequence
    if (command == 's' || command == 'S') {
      if (!motor4Frozen) {
        // First 's' press: freeze motor 4 and start perturbation sequence
        motor4Frozen = true;
        baseTension1 = targetTension1;
        baseTension2 = targetTension2;
        baseTension3 = targetTension3;
        perturbationIndex = 0;
        motorIndex = 0;
        targetTension1 = baseTension1 + perturbations[0];
        Serial.print("Motor 4 frozen. Perturbation "); Serial.print(perturbations[0], 2);
        Serial.println(" applied to Motor 1.");
        Serial.print("New targets: M1="); Serial.print(targetTension1, 2);
        Serial.print(" M2="); Serial.print(targetTension2, 2);
        Serial.print(" M3="); Serial.println(targetTension3, 2);
      } else {
        // Remove perturbation from current motor before moving on
        if (motorIndex == 0) {
          targetTension1 = baseTension1;
          Serial.print("Perturbation removed from Motor 1. M1=");
          Serial.println(targetTension1, 2);
        } else if (motorIndex == 1) {
          targetTension2 = baseTension2;
          Serial.print("Perturbation removed from Motor 2. M2=");
          Serial.println(targetTension2, 2);
        } else if (motorIndex == 2) {
          targetTension3 = baseTension3;
          Serial.print("Perturbation removed from Motor 3. M3=");
          Serial.println(targetTension3, 2);
        }
        
        // Move to next motor
        motorIndex++;
        
        if (motorIndex > 2) {
          // Finished all 3 motors for current perturbation, move to next
          motorIndex = 0;
          perturbationIndex++;
          
          if (perturbationIndex >= numPerturbations) {
            // All perturbations complete - act like 'c'
            targetTension1 = 0;
            targetTension2 = 0;
            targetTension3 = 0;
            targetTension4 = 0;
            motor4Frozen = false;
            returningToZero = true;
            perturbationIndex = 0;
            motorIndex = 0;
            Serial.println("\nAll perturbations complete. Returning to zero.");
            while (Serial.available() > 0) Serial.read();
            return;
          }
        }
        
        // Apply current perturbation to current motor
        if (motorIndex == 0) {
          targetTension1 = baseTension1 + perturbations[perturbationIndex];
          Serial.print("Perturbation "); Serial.print(perturbations[perturbationIndex], 2);
          Serial.println(" applied to Motor 1.");
        } else if (motorIndex == 1) {
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

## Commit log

2025-07-11 update 7/11/2025
    [Force Meter Stand.SLDPRT, Load Cell Assembly.SLDASM, Load Cell Axial part.SLDPRT, Load Cell Base V2.SLDPRT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]
2025-08-27 new
    8/27/2025
    [6_Axis_FT_Sensor_Log.csv, ATI-9105-TW-Mini40-R-X_X-IP65.SLDPRT, Basic Force Sensor.SLDPRT, Basic_Force_Sensor_Stand.SLDPRT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]
2025-08-28 New
    8/28/2025
    [6_Axis_FT_Sensor_Log.csv, ATI_Sensor_Log.csv, Angled_Mount_Assembly.SLDASM, Angled_Mount_Base.SLDPRT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]
2025-08-29 new
    9/29/2025
    [Distributed_Load_Attachment.STL, Distributed_Load_Attachment_TPU.SLDPRT]
2025-09-07 Before 3 tendon
    [4390N113_Flanged Ultra-Thin Ball Bearing.SLDPRT, 625ZZ.SLDPRT, ATI_Sensor_Log(2.0to1.0).csv, Capstan Assembly.SLDASM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]
2025-09-11 Before 3 tendons
    [4390N113_Flanged Ultra-Thin Ball Bearing.SLDPRT, 57155K472_Flanged Ball Bearing.SLDPRT, 625ZZ.SLDPRT, ATI-9105-TW-Mini40-R-X_X-IP65.SLDPRT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]
2025-09-16 Winch + Force Frame
    9/16/2025
    [5972K245_Ball Bearing.SLDPRT, 6656K142_Ultra-Thin Ball Bearing.SLDPRT, Azimuth Bar.SLDPRT, Azimuth Bracket.SLDPRT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]
2025-09-26 New Frame
    9/25/2025
    [ATI_Sensor_Log.csv, Angled_Mount_Assembly.SLDASM, Angled_Mount_Base.SLDPRT, Angled_Mount_Slider.SLDPRT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]
2025-10-01 optimized beam
    10/1/25
    [Final Beam.SLDPRT, Optimized Beam.SLDPRT, Validation(2.0to1.0)(3tendon)(10-1-25).xlsx]
2025-10-02 JMP
    10/02/2025
    [ATI_Sensor_Log.csv, Force Application Bar.SLDPRT, Validation.xlsx]
2025-10-05 with vailidation data
    10/06/2025
    [ATI-9105-TW-Mini40-R-X_X-IP65.SLDPRT, ATI_Sensor_Log.csv, Azimuth Beam.SLDPRT, Big Pully.SLDPRT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]
2025-10-09 single and double hardware point force data
    10/8/2025
    [ATI_Sensor_Log.csv, Final Beam.SLDPRT, Sort of Custom Design by roll, pitch, s, F, tau1.xlsx, Sort of Sort of Custom Design.xlsx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]
2025-10-11 add_noise
    10-11-2025
    [Validation(1.5)(3tendon).xlsx, Validation(1.75)(3tendon).xlsx, Validation(2.00to1.25)(3tendon).xlsx, testdata.xlsx]
2025-10-17 Tidy up of folders
    10/17/2025
    [ATI_Sensor_Log(2.0to1.0).csv, ATI_Sensor_Log.csv, Sort of Custom Design by roll, pitch, s, F, tau1.xlsx, Sort of Sort of Custom Design.xlsx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]
2025-10-19 Micro perturb working
    10/18/2025
    [ATI_Sensor_Log.csv, Sort of Custom Design by el1, s1, F1, el2, s2, F2, tau1.xlsx, Validation(2.00to1.25)(3tendon).xlsx, testdata.xlsx]
2025-10-20 even better micro perturbation
    10/20/2025
    [Validation(2.00to1.25)(3tendon).xlsx, testdata.xlsx]
2025-10-21 two force with micro perturb full results
    [ATI_Sensor_Log.csv, Validation(1.5)(3tendon).xlsx, testdata.xlsx]
2025-10-28 pairwise_distance
    10/28/2025
    [ATI_Sensor_Log.csv, Validation(1.5)(3tendon).xlsx, Validation(2.00to1.25)(3tendon).xlsx]
2025-11-05 1st commit of new branch
    11/4/2025
    [Validation(1.5)(3tendon).xlsx]
2025-11-06 Pre topology opt + purterbations
    11/5/2025
    [Validation(1.5)(3tendon).xlsx, Validation(2.00to1.25)(3tendon).xlsx, testdata.xlsx]
2025-11-10 micro perturb w results
    11/10/2025
    [ATI_Sensor_Log.csv, Sort of Custom Design by s, F.xlsx, Validation(1.5)(3tendon).xlsx, Validation(1.75)(3tendon).xlsx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]
2025-11-13 refined code for perturbation based sensing
    11/12/2025
    [Validation(1.5)(3tendon).xlsx, Validation(1.7to1.25)(3tendon).xlsx, testdata.xlsx]
2025-12-11 Two force estimation working in hardware (12/11/2025)
    [ATI_Sensor_Log.csv, Sigma Wrench Calcs.xlsx, Sort of Custom Design by theta1, theta2, s1, s2, F1, F2.xlsx, Validation(SVD)(3tendon).xlsx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]
2025-12-20 Working 12/20/2025
    [ATI_Sensor_Log.csv, Sigma Wrench Calcs.xlsx, Sort of Custom Design by el1, s1, F1, el2, s2, F2, tau1.xlsx, Sort of Custom Design by s, F.xlsx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]
2025-12-24 New Figure and Plot Lighting
    [working beam don't delete.xlsx]
2026-01-06 After Christmas before Tendon addition 1/5/2026
    [working beam don't delete.xlsx]
2026-01-07 Tendons added 1/7/2026
2026-01-15 Before sigmoid actuation function 1/15/2026
    [ATI_Sensor_Log.csv, Noise Calculation.xlsx, Validation(1.5)(3tendon).xlsx, Validation(SVD)(3tendon).xlsx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]
2026-01-23 Hardware and Electronic Changes 1/22/2026
    [Azimuth Beam.SLDPRT, Big Pully.SLDPRT, Bracket.SLDPRT, Electronics Box.SLDPRT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]
2026-02-02 Figures & CAD 2/2/2026
    [New Base.SLDPRT, Sensor_Beam_Adapter.SLDPRT]
2026-02-14 Before John Feedback 2-13-2026
    [ATI-9105-TW-Mini40-R-X_X-IP65.SLDPRT, Big Pully.SLDPRT, Flexure Mechanism.SLDPRT, Horizontal Spin Top.SLDPRT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]
2026-02-19 Adjustments after 1st design optimization run (2-19-2025)
    New constraint function
    New test force sampling
    New 6mm max radius
    [Design 2-14-2026.xlsx, Optimal Beam.SLDPRT, Optimized Beam.SLDPRT, VBA Macro Beam.SLDPRT]
2026-02-20 more fixes (2-19-2026)
    Optimal Beam CAD
    Fixed global search by increasing lower bound
    Added spreadsheet history for design optimization
    [Design (2-14-2026).xlsx, Design (2-19-2026).xlsx, Design 2-14-2026.xlsx, Design_Optimization_Results.xlsx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]
2026-02-25 Fixes (2-25-2026)
    - Fixed phi 1 being dead variable in design opt
    - Changed design opt FD step size to 1e-4 to overcome numerical noise of model.
    - Deleted some old functions
    -
    [Design (2-19-2026).xlsx, Design_Optimization_Results.xlsx, Global_Search_Results.xlsx, Local_Refinement_Results.xlsx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]
2026-02-26 fix ellipse stress calc
    Refactor MATLAB design pipeline and correct stress calculations.
    - calc_ellipse_vonmises: renamed parameters to (a,b,...), corrected Iy/Iz formulas and von Mises/torsion computation, simplified max stress and FOS calculation.
    - design_optimization: added expand_design support (including new "circular_uniform" mode), changed how fixed variables are handled for fmincon, and updated objective/constraint calls to match new si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
    - update_design: simplified function signature (removed design_name), clarified r layout, reorganized try/catch and update/save flow, and fixed per-link updates (E, color, tendon transforms, UpdateAl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
    - Added/updated binaries: Global_Sear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
    [Global_Search_Results.xlsx, Local_Refinement_Results.xlsx, Optimal Beam.SLDPRT]
2026-02-27 Refactor Arduino tension control
    Rewrote the Arduino tension-control firmware so each motor steps independently using non-blocking, delay-based pulses instead of the old adaptive microstep routine. Microsteps are now fixed at 256, m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
    On the file-organization side, calibration and experiment assets were reorganized under a Calibration/ folder, including winch calibration data, ATI sensor calibration files, sensor logs, and an opti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
    [ATI_Sensor_Log.csv, Optimal Design.xlsx, Winch Calibration Curve.xlsx]
2026-04-24 Added Sorosim toolbox to repo
    [Optimal Design.xlsx]
